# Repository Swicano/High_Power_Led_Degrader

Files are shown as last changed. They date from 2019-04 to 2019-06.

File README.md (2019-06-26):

# High_Power_Led_Degrader
All the information regarding the construction and running of the "Blue Box Sr." built to drive 600W worth of LED CoBs using water cooling. This device builds on the unrealized desires and lessons learned from the building and running of the first generation photothermal degrader, now renamed the "Blue Box Jr."

This repository includes the electrical schematic, the 3D print files used to make the interface, and the arduino code that runs the entire device. The device features 6 100W LED Cobs, each driven by their own power stage, and independently feedback controlled. The control is run by a Arduino Leonardo (ATmega32u4) and features FSM user interface, and software interrupt driven safety for overtemp, overpower, and chamber opening.

<p>
<p align="center"> The Bigger Blue-er Box </p>
<p align="center">
    The finished Degrader running 
</p>
<p>
<p align="center">
    Power and Control The Irradiation Chamber 
<p align="center"> (left) the power and control unit. (right) the light source within the irradiation chamber </p>
</p>

The completion of Blue Box Jr increased the sample degradation throughput by 5x, but there was some clear downsides. One was the way in which it allowed the test chamber to be heated by the exhaust air coming from the LED array. Another was the inverted design, though advantageous for the degradation, it removed the feasibility of more "natural" tests such as simulating litter or oceanic litter. Then of course there was the desires. We wanted bigger, brighter, power-tuning, and above all, sample flexibility.

The design of Blue Box Sr was built around the idea of switching from an array of 3W single LEDs to an array of 100W blue LED CoBs from Chanzon an array of arrays. With this huge increase in not only total heat, but heat density, water cooling was the natural deicions to solve our sample chamber heating problem. Since the building is wired with chilled water, this was a rather simple thing to implement, but also led to separating the water-cooled irradiation chamber from the high powered electronics into two devices. 

All of the above decisions were the thinking (with guidance) of an undergraduate senior design team, which created the first iteration of the device. Once their semester ended, and they traded a product for a grade, I was left with the task of turning this device from "group project" into a usable laboratory device. A picture gallery is available [here](Coming_Soon) of the journey. The major modifications I made were:

* Complete redesign of the Power and Control unit:
  * A new, less flammable, more breathable housing
  * Addition of current and voltage sensing to monitor LED power
  * Ability to vary LED power based on the above, programatically
  * Rewrite of the control code  
* Increased the usable volume of the irradiation chamber and the sample door
* Added watercooling to the floor of the chamber after discovering that the bright LEDs
* For fun, added 3d printed parts wherever I could

<p>
<p align="center">
    Power and Control The Irradiation Chamber 
<p align="center"> (left) Testing the Power modulation circuitry (right) testing the water cooling effectiveness </p>
</p>

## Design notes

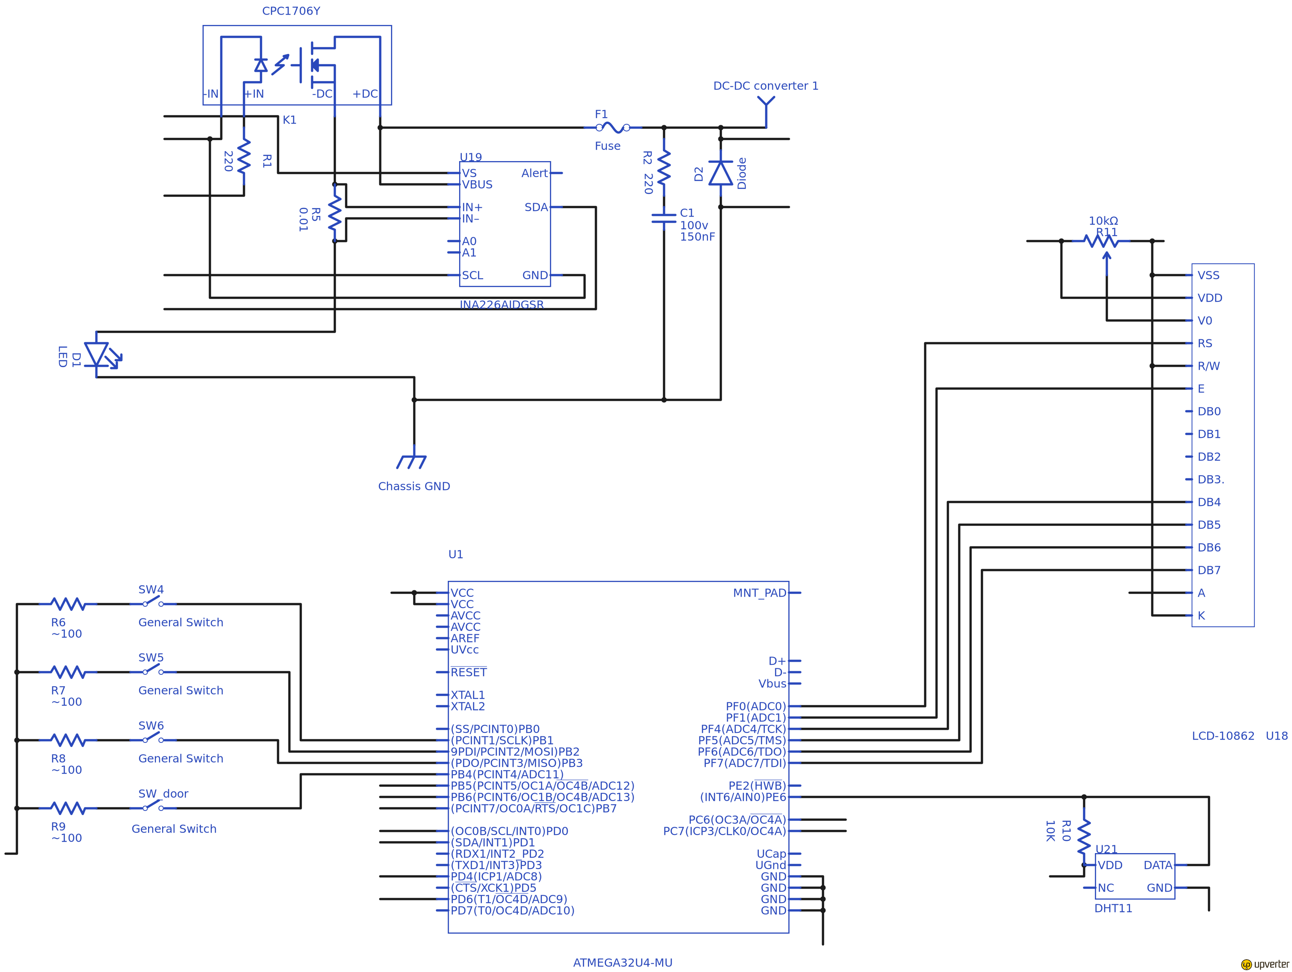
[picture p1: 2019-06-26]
SchematicFiles/Blue-Box-Sr-hd-default.png

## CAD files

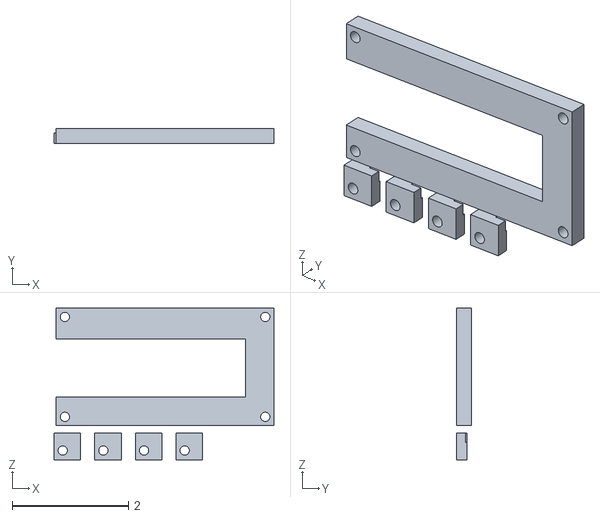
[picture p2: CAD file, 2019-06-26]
3DPrintFiles/LCD mounting bracket v4.stl
3.79 x 0.25 x 2.61

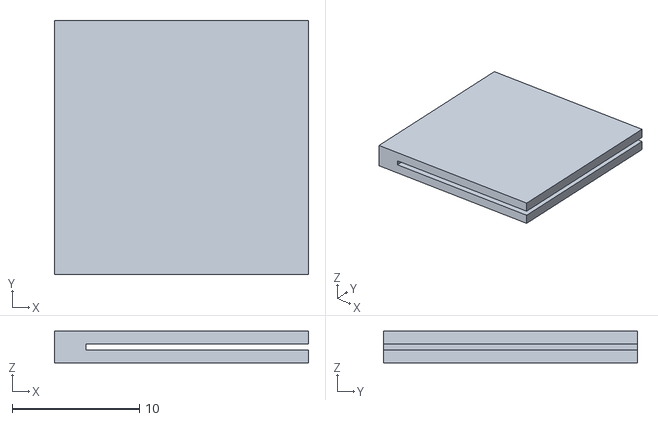
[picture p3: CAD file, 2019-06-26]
3DPrintFiles/ribbonClips v2.stl
20.0 x 20.0 x 2.50

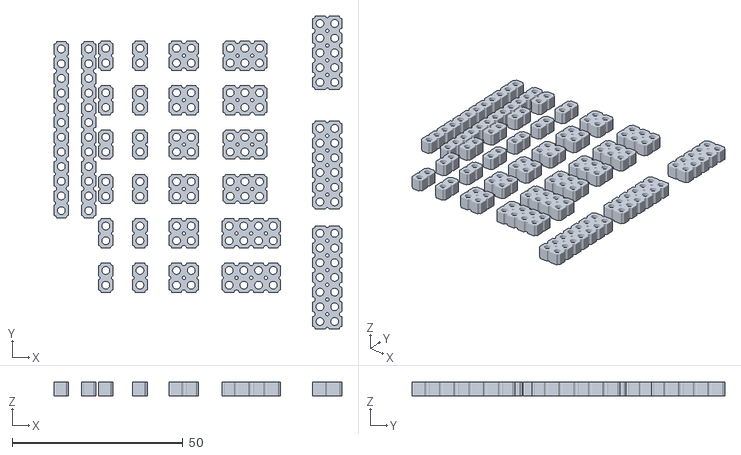
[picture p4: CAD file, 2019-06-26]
3DPrintFiles/cable combs v8.stl
84.3 x 91.5 x 4.00

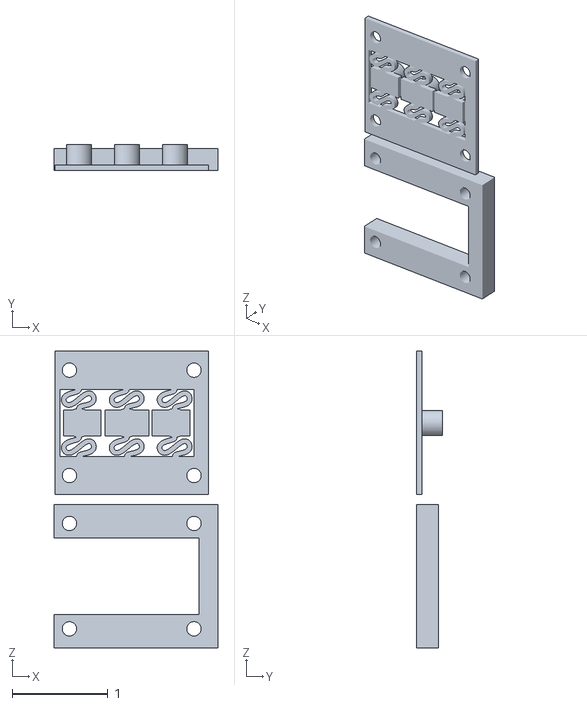
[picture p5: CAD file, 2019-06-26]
3DPrintFiles/button holder v6.stl
1.71 x 0.275 x 3.10

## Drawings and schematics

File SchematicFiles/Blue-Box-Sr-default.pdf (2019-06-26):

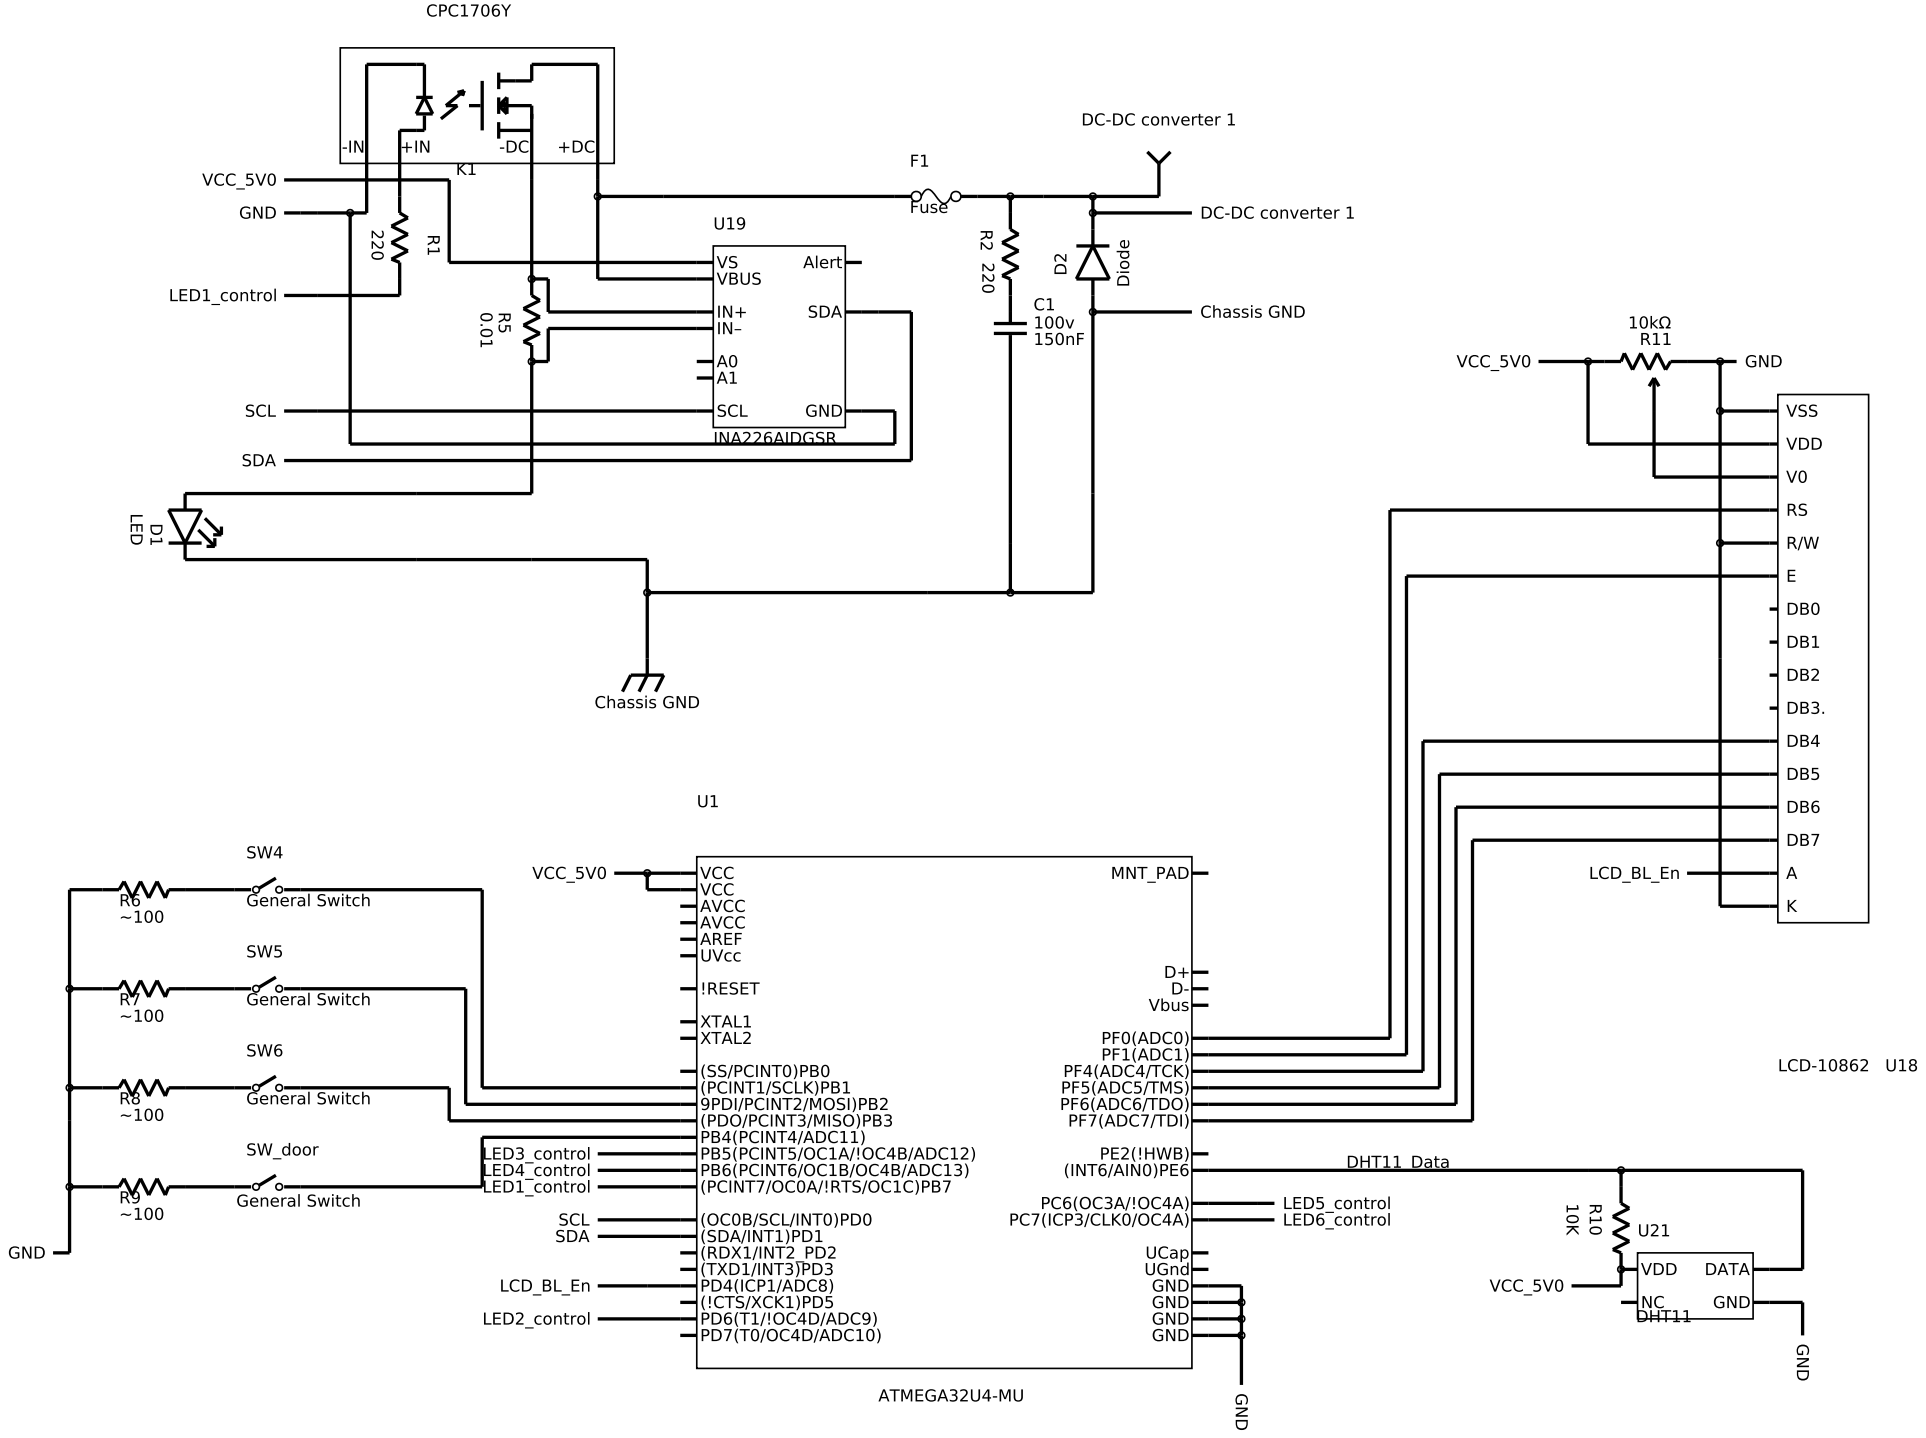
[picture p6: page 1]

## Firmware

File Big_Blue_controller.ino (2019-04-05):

// include the library code:
#include <LiquidCrystal.h>
#include <DHT.h>
#include <INA226.h>
#include <Wire.h>

/* Pin List: (by "physical pin", aka, pin 36 below is also IDE pin 14, IDE analog pin A0, ADC7, PF7, and TDI)
 * 00  - xxxxxx     10  - Button 2       20  - xxxxxx     30  - LED SSR 3 40  - LCD  
 * 01  - DHT11_Data 11  - Button 3       21  - xxxxxx     31  - LED SSR 6 41  - LCD  
 * 02  - xxxxxx     12  - LED SSR 4      22  - xxxxxx     32  - LED SSR 1 42  - xxxxxx  
 * 03  - xxxxxx     13  - xxxxxx         23  - xxxxxx     33  - xxxxxx    43  - xxxxxx  
 * 04  - LCD_bl     14  - xxxxxx         24  - xxxxxx     34  - xxxxxx    44  - xxxxxx  
 * 05  - xxxxxx     15  - xxxxxx         25  - LCD_BL_En  35  - xxxxxx    45  - xxxxxx  
 * 06  - xxxxxx     16  - xxxxxx         26  - LED SSR 2  36  - LCD       46  - xxxxxx    
 * 07  - xxxxxx     17  - xxxxxx         27  - xxxxxx     37  - LCD       47  - xxxxxx  
 * 08  - xxxxxx     18  - I2C BUS Clock  28  - Door Sense 38  - LCD       48  - xxxxxx  
 * 09  - Button 1   19  - I2C BUS Data   29  - LED SSR 5  39  - LCD       49  - xxxxxx  
 *
 */ 

/* IN ORDER TO ADD A NEW STATE YOU MUST MODIFY THESE PLACES:
 **   Variables:
 ***    num_menu_states
 ***    menu_states
 ***    transition_select   <-- these can be tricky to do correctly
 ***    transition_up       <--/  dont just add the new state to
 ***    transition_down     <--/  the end of the list.
 **   Functions:
 ***    UpdateMenu(int state)
 ***    pressUP(int state)
 ***    pressDOWN(int state)
 ***    pressSELECT(int state)
 * PLUS whatever code you need to make that state work   
 */ 

// Variables associated with the overarching system---------//
// were a button pressed                                    //
volatile bool PCFlag = false;                               //
int numtoUpdate = 15;                                       //
int sysStep = 0;                                            //
int serialDelay = 30;                                       //
int serialCounter = 0;                                      //
                                                            //
//  status issues are arranged in most pressing to least    //
//    0b00000000 - all fine               "RUNNING"         //
//    0b00000001 - door open              "DOOR   "         //
//    0b00000010 - over Temp              "TEMP   "         //
//    0b00000100 - led issue              "LED!   "         //
//    0b00111000 - reserved for future use                  //
//    0b01000000 - run finished           "DONE   "         // 
//    0b10000000 - run not started yet    "IDLE   "         //
byte statusByte = 0b10000000;                               //
const char *statusOptions[9] = { "RUNNING", "DOOR   ", "TEMP   ","LED!   ","UNKNOWN","UNKNOWN","UNKNOWN", "DONE   ", "IDLE   "  };
char *statusString = NULL;                                  //
//----------------------------------------------------------//

// Variables and consts associated with the timer subsystem-------------//
const long MILLIINDAY = 86400000;                                       //
const long MILLIINHOUR = 3600000;                                       //
const long MILLIINMIN = 60000;                                          //
const long MILLIINSEC = 1000;                                           //
unsigned long millisStart = millis(); //time of run start               //
unsigned long millisElapse = millis();                                  //
char timeElapse[] = "10D12:51:11";                                      //
unsigned long millisSet = millis()+40000;                               //
char timeSet[] = "20D09:42:22";                                         //
unsigned long millisRemain = millis();                                  //
char timeRemain[] = "30D07:33:33";                                      //
                                                                        //
// These timers down here set how often things                          //
// get updated in the main loop.                                        //
// no need for timers since we're not fancy                             //
const long updatePeriod = 1000L;//ms                                    //
const long updateSubPeriod = updatePeriod/numtoUpdate;                  //
unsigned long updateTimer = millis()+updateSubPeriod;                   //
// we need one more lcd time-out timer                                  //
unsigned long millisScreenTimeOut = millis()+15000L;                    //
const int screenTimeOutPeriod = 15000;                                  //
//----------------------------------------------------------------------//


//Variables associated with the temp measurement subsystem--//
const int DHTPIN1 = 7;                                      //
DHT dht(DHTPIN1, DHT11);                                    //
int tempCurr = 35;                                          //
int tempLimit = 38;                                         //
//----------------------------------------------------------//


//Variables associated with the power measurement subsystem-//
const int numLEDS = 6;                                      //
INA226 ina0;                                                //
INA226 ina1;                                                //
INA226 ina2;                                                //
INA226 ina3;                                                //
INA226 ina4;                                                //
INA226 ina5;                                                //
//uint64_t inaptr[] = {&ina0,&ina1,&ina2,&ina3,&ina4,&ina5};  // 

//const int i2cAddr[] = {0x40,0x40,0x42,0x40,0x40,0x40};            // TEMPORARY
const int i2cAddr[] = {0x40,0x41,0x42,0x44,0x45,0x46};            // permanent
//                          //___|__A1_|__A0_|_             //
//int i2cAddr0 = 0x40;      //   | GND | GND |              //
//int i2cAddr1 = 0x41;      //   | GND |  VS |              //
//int i2cAddr2 = 0x42;      //   | GND | SDA |              //
//int i2cAddr3 = 0x44;      //   |  VS | GND |              //
//int i2cAddr4 = 0x45;      //   |  VS |  VS |              //
//int i2cAddr5 = 0x46;      //   |  VS | SDA |              //

int powTarget = 5;                                         //
int pinLevel[] = {5, 5, 5, 5, 5, 5};            // arduino claims all pins go 0-255 by default
//const int pinLED[] = {10,10,11,10,10,10}; // Temporary Dummy pins
const int pinLED[] = {10,9,11,6,13,5};                      // the pins used for the led control //                                                            //
int powLimit = 100; // Watts                                //
float powLED[] = {0,0,0,0,0,0};                   //
unsigned long enerLED[] = {0,0,0,0,0,0};                    //
float voltLED[] = {3.5,3.4,3.3,3.2,3.1,3.7};                //
float currLED[] = {3.1,3.1,3.1,3.1,3.1,3.1};                //
//----------------------------------------------------------//

// Variables associated with the LCD subsystem--------------//
// associate any needed LCD interface pin                   //
const int rs = A0, en = A1, d4 = A2, d5 = A3,               //
        d6 = A4, d7 = A5, bl = 4;                           // 
  //bl is for backlight PWM control, contr is PWM contrast  //
LiquidCrystal lcd(rs, en, d4, d5, d6, d7);                  //
int lcdbright = 50;                                         //
//int lcdcontr = 50;                                          // permanent
int buzzervol = 100;                                        //
                                                            //
byte degC[8] = {  //creates the deg C symbol                //
  0b11000,                                                  //
  0b11000,                                                  //
  0b00110,                                                  //
  0b01001,                                                  //
  0b01000,                                                  //
  0b01001,                                                  //
  0b00110,                                                  //
  0b00000,                                                  //
};                                                          //
byte invertS[8] = {  // inverted S symbol for start/stop    //
  0b10001,                                                  //
  0b01110,                                                  //
  0b01111,                                                  //
  0b10001,                                                  //
  0b11110,                                                  //
  0b01110,                                                  //
  0b10001,                                                  //
  0b00000,                                                  //
};                                                          //
//----------------------------------------------------------//

//--variable associating with button press detection----------------------------------------------------------//
int buttonID = 0;     // where i determing WHICH button was pressed                                           //
byte lastPinB = 0;    // need the last value of PINB register to determine if a RISING edge is found or not   //
byte PinB = 0;        // store the truncated current PINB values for PB1,2,3 only                             //
//volatile bool PCFlag = false; // tell the program that the PCINT happened                                   //
//------------------------------------------------------------------------------------------------------------//
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

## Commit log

2019-04-05 Main control code for Arduino Leonardo
    implements dual Finite-State Machines, one to run the state of the box, another to run the LCD menu system, implemented without a FSM library to save code space
2019-06-26 added 3d files and schematic
    [LCD mounting bracket v4.stl, button holder v6.stl, cable combs v8.stl, ribbonClips v2.stl]
